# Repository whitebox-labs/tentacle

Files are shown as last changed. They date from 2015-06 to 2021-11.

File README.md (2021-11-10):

# Whitebox Labs Tentacle Shield for Arduino
`Models T1.15A, T1.16`

Tentacle Shield

## What's the Tentacle Shield?
An Arduino shield to host and individually isolate up to 4 EZO Circuits from Atlas Scientific to measure PH, Dissolved Oxygen, Electric Conductivity (E.C.), Oxidation-Reduction Potential (ORP) and RTD (Temperature).

* 4 channels
* 5V only

Individually isolated measurement circuits and communication lines prevent noise and ground loops for precise measurements even in closed-loop systems.

## Getting Started
* [Documentation Site](https://www.whiteboxes.ch/docs/tentacle/t1)
* Download the [Setup Sketch](https://raw.githubusercontent.com/whitebox-labs/tentacle-examples/master/arduino/tentacle-setup/tentacle_setup/tentacle_setup.ino)
* [Quick Start Tutorial](https://www.whiteboxes.ch/docs/tentacle/t1/#/quickstart)

## Code Examples
* [Continuous readings](https://www.whiteboxes.ch/docs/tentacle/t1/#/continuous-example)
* [Continuous, asynchronous readings](https://www.whiteboxes.ch/docs/tentacle/t1/#/asynchronous-example)
* [Interactive, bidirectional communications](https://www.whiteboxes.ch/docs/tentacle/t1/#/interactive-example)
* [Examples Git Repository](https://github.com/whitebox-labs/tentacle-examples) `git clone https://github.com/whitebox-labs/tentacle-examples.git`
* [Download all examples (zip)](https://github.com/whitebox-labs/tentacle-examples/archive/master.zip)

## Downloads
* [Tentacle Setup sketch](https://raw.githubusercontent.com/whitebox-labs/tentacle-examples/master/arduino/tentacle-setup/tentacle_setup/tentacle_setup.ino)
* [T1.16 3D-Model (STL)](https://github.com/whitebox-labs/tentacle/blob/master/hardware/mechanical/tentacle_t1.STL)
* [T1.16 3D-Model (STEP)](https://github.com/whitebox-labs/tentacle/blob/master/hardware/mechanical/tentacle_t1.STEP)
* [T1.16 Mechanical Drawing (PDF)](https://github.com/whitebox-labs/tentacle/raw/master/hardware/mechanical/tentacle_t1_mechanical.pdf)
* [BNC Connector Mechanical Drawing (PDF)](https://github.com/whitebox-labs/tentacle/raw/master/hardware/mechanical/bnc_mechanical.pdf)
* [T1.16 Schematic (PDF)](https://github.com/whitebox-labs/tentacle/raw/master/hardware/tentacle_schematic.pdf)

## Support
For customer support, please use the [contact form](https://www.whiteboxes.ch/contact/) on our website.

If you find bug in the documentation, examples or the schematic, feel free to create an issue or even a pull request here on GitHub. 

## Open Source
The Tentacle Shield is [certified](http://certificate.oshwa.org/certification-directory/) Open Source Hardware with UID CH000003. Schematics and layout are licensed under [Creative Commons BY-SA 4.0](http://creativecommons.org/licenses/by-sa/4.0/). Silkscreen graphics and the trade mark “Tentacle” are intellectual property of Whitebox Labs

* [Hardware source files on GitHub](https://github.com/whitebox-labs/tentacle) `git clone https://github.com/whitebox-labs/tentacle.git`

Made with KiCAD logo (http://kicad.org/)

## Buy
* From [our store](https://www.whiteboxes.ch/) – we ship worldwide
* or from one of our [Distributors](https://www.whiteboxes.ch/distributors)

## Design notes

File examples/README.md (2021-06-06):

examples moved here:

https://github.com/whitebox-labs/whitebox-arduino-example-code

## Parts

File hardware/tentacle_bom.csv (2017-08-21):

Id | Description | Package | Qty | Designator | Designation
1 | 1x6-pin female header .1inch | .1 inch header | 1 | SHIELD1 | ARDUINO_SHIELD
2 | 1x8-pin female header .1inch | .1 inch header | 2 | SHIELD1 | ARDUINO_SHIELD
3 | 1x10-pin female header .1inch | .1 inch header | 1 | SHIELD1 | ARDUINO_SHIELD
4 | LDO voltage regulator | SOT89 | 4 | REG1,REG2,REG3,REG4 | LD2981ABU50TR
5 | UART multiplexer | SO16N | 1 | MUX1 | 74HCT4052D122
6 | Digital signal isolator | so-8 | 4 | SIG_ISO2,SIG_ISO3,SIG_ISO4,SIG_ISO1 | SI8600
7 | SMD resistor 4.7K, 1/8W | SM0805 | 19 | R16,R14,R12,R10,R8,R6,R4,R2,R17,R3,R1,R7,R5,R9,R11,R13,R15,R18,R19 | 4.7K
8 | Multilayer Ceramic Capacitor 0.1uF | SM0805 | 8 | C4,C9,C14,C19,C10,C5,C15,C20 | 0.1 µF
9 | Multilayer Ceramic Capacitor 1uF | SM0805 | 8 | C12,C2,C7,C17,C1,C6,C11,C16 | 1µF
10 | Multilayer Ceramic Capacitor 2.2uF | SM0805 | 4 | C3,C8,C13,C18 | 2.2µF
11 | Tantalum Capacitor 470uF | c_tant_x | 1 | C21 | 470µF
12 | 1x3 male pin headers .1inch | 1x3 .1 inch spacing male pin | 1 | JP9 | JUMPER3
13 | 2x3 male pin headers .1inch | 2x3 .1 inch spacing male pin | 4 | JP1,JP3,JP5,JP7,JP2,JP4,JP6,JP8 | JUMPER3
14 | Tactile push button | B3S-1000P | 1 | SW1 | SW_PUSH
15 | Isolated DC/DC converter 5V | R1SE_0505 | 4 | DCDC1,DCDC2,DCDC3,DCDC4 | R1SE_0505
16 | BNC Connector | BNC-1337542 | 4 | P1,P2,P3,P4 | BNC
17 | 1x3-pin female header .1inch | 1x3 .1 inch spacing female pin | 8 | STP1,STP2,STP3,STP4 | ATLAS_STAMP
18 | Shorting jumper .1inch | .1 inch jumper | 9 | JP* | JUMPER, JUMPER3

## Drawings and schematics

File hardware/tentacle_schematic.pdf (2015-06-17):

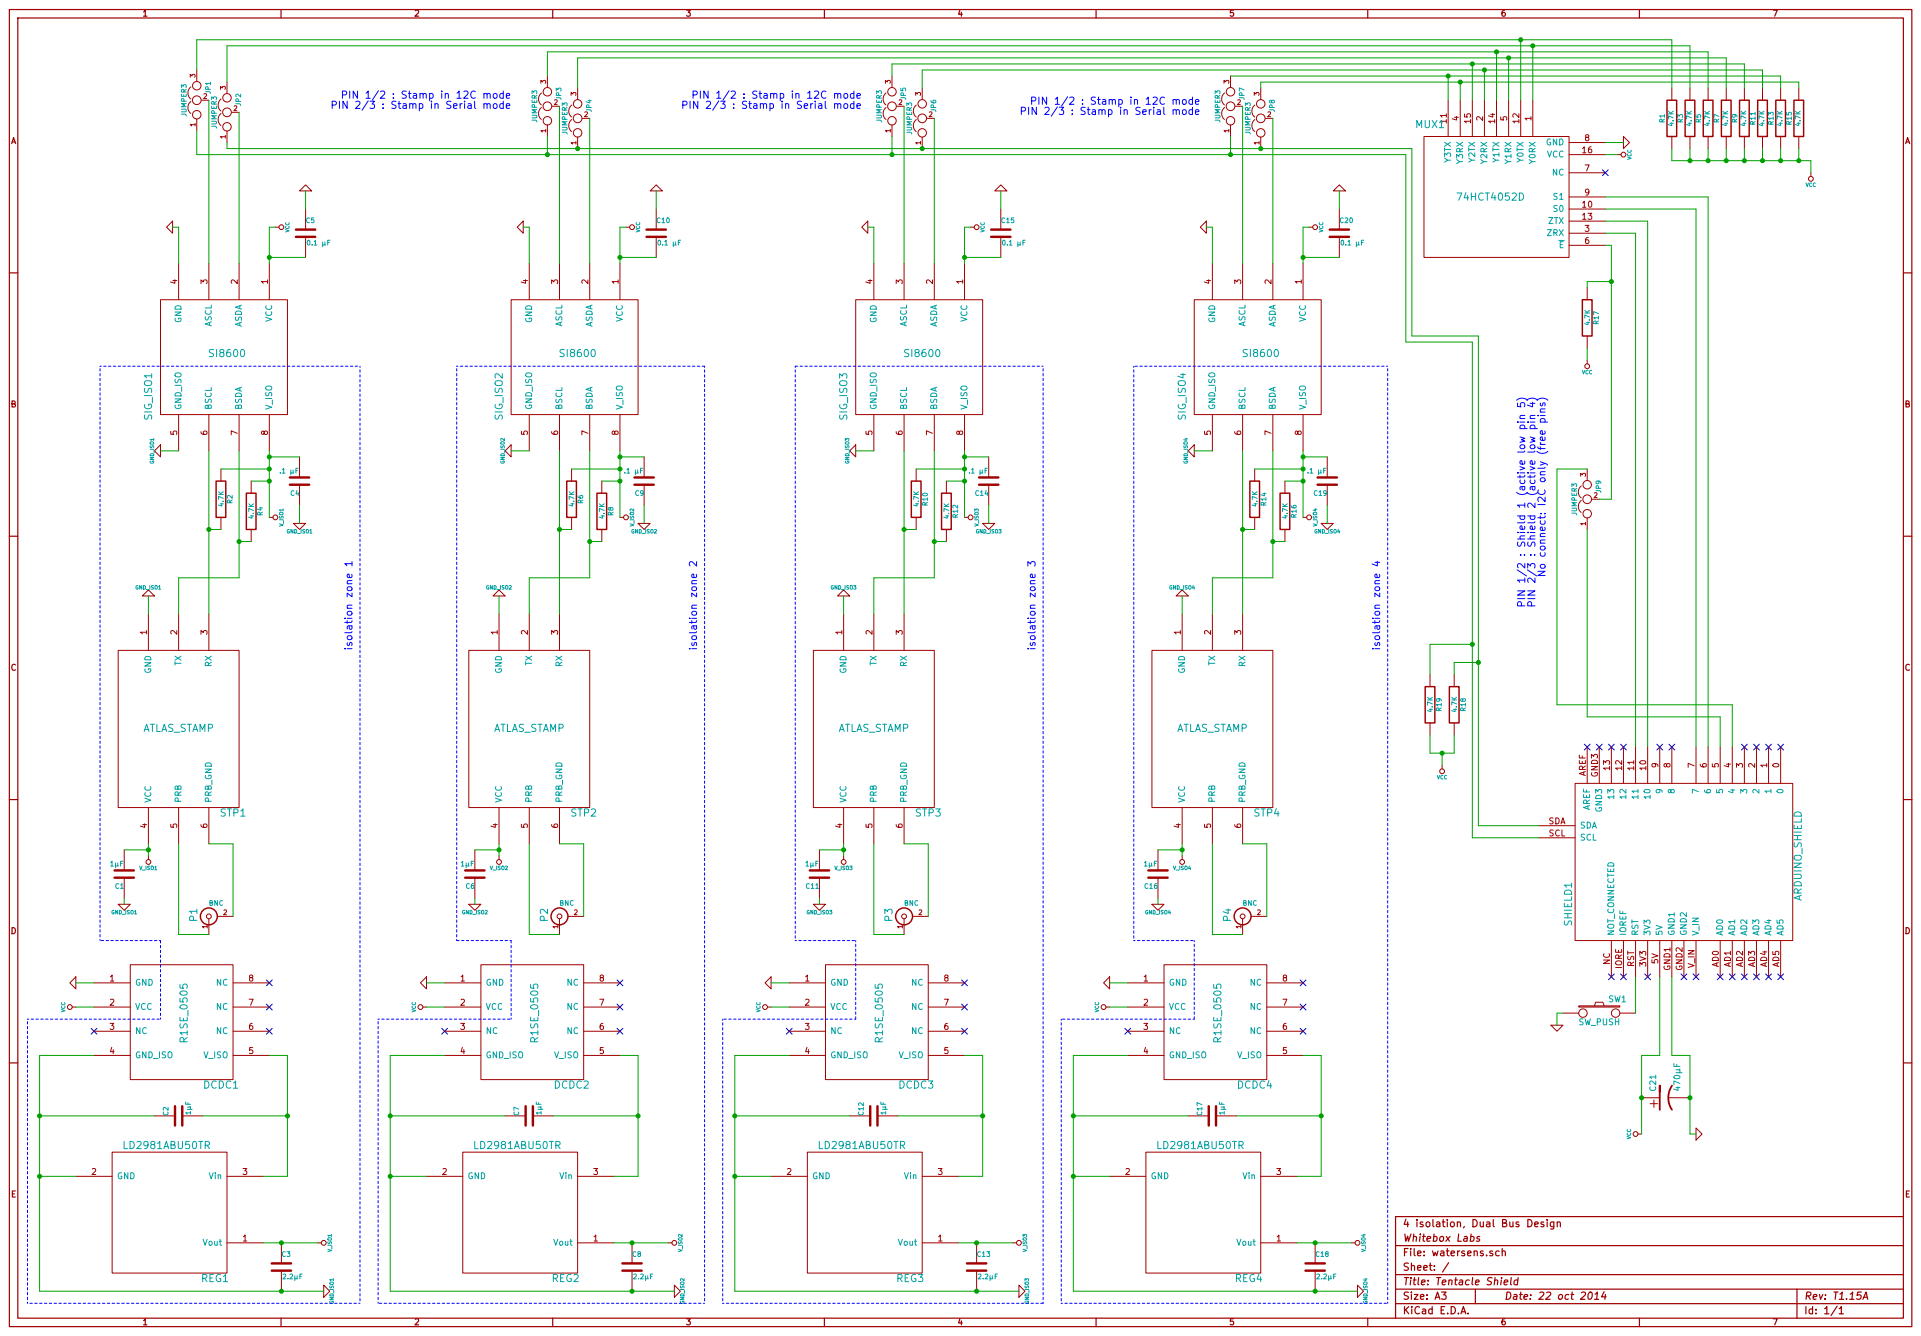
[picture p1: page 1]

3 JP7 JUMPER3
Title: Tentacle Shield File: watersens.sch Sheet: / Whitebox Labs 4 isolation, Dual Bus Design Y0RX

PIN 1/2 : Stamp in 12C mode
PIN 2/3 : Stamp in Serial mode

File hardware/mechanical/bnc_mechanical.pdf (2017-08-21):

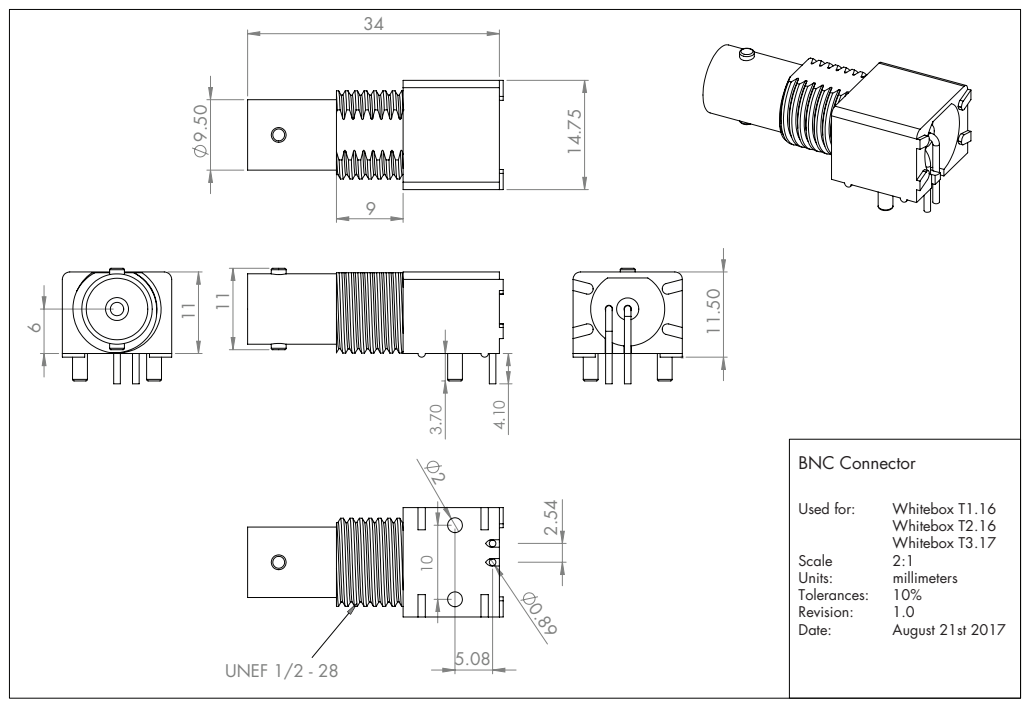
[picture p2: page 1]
UNEF 1/2 - 28; BNC Connector; Used for:; Whitebox T1.16; Whitebox T2.16 Whitebox T3.17; Scale; Units:; millimeters; Tolerances:; Revision:; Date:; August 21st 2017

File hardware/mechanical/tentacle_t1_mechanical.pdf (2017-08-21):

50.80 | 77.40

1.30

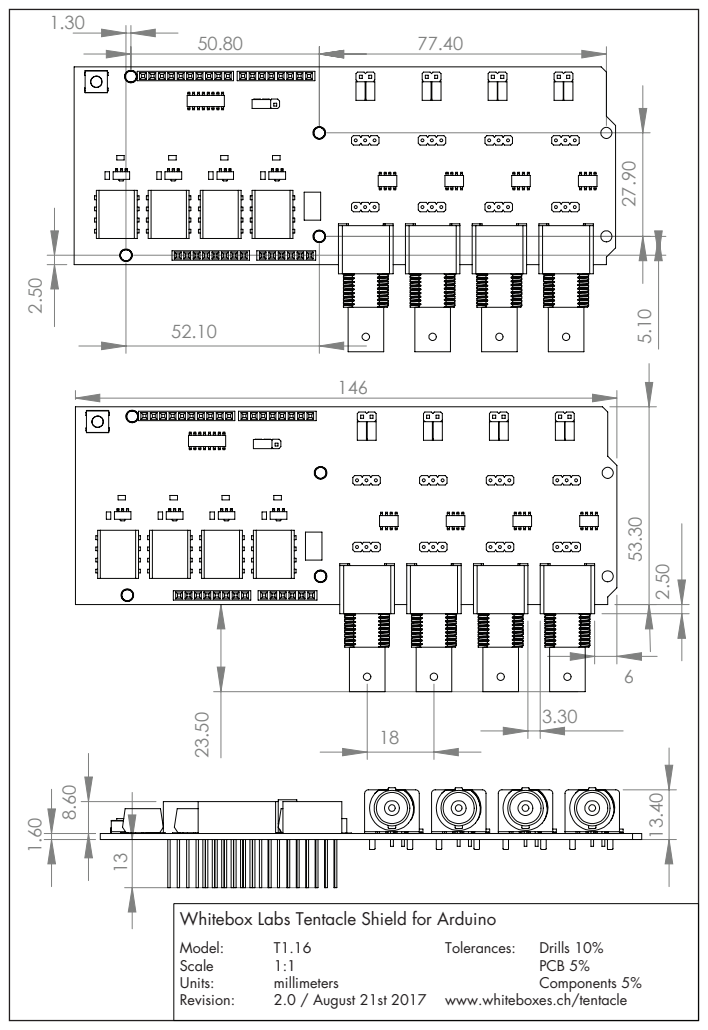
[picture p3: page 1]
Tolerances:; Drills 10%; PCB 5% Components 5%; Model:; Scale; Units:; millimeters; Revision:; 2.0 / August 21st 2017

Whitebox Labs Tentacle Shield for Arduino

www.whiteboxes.ch/tentacle

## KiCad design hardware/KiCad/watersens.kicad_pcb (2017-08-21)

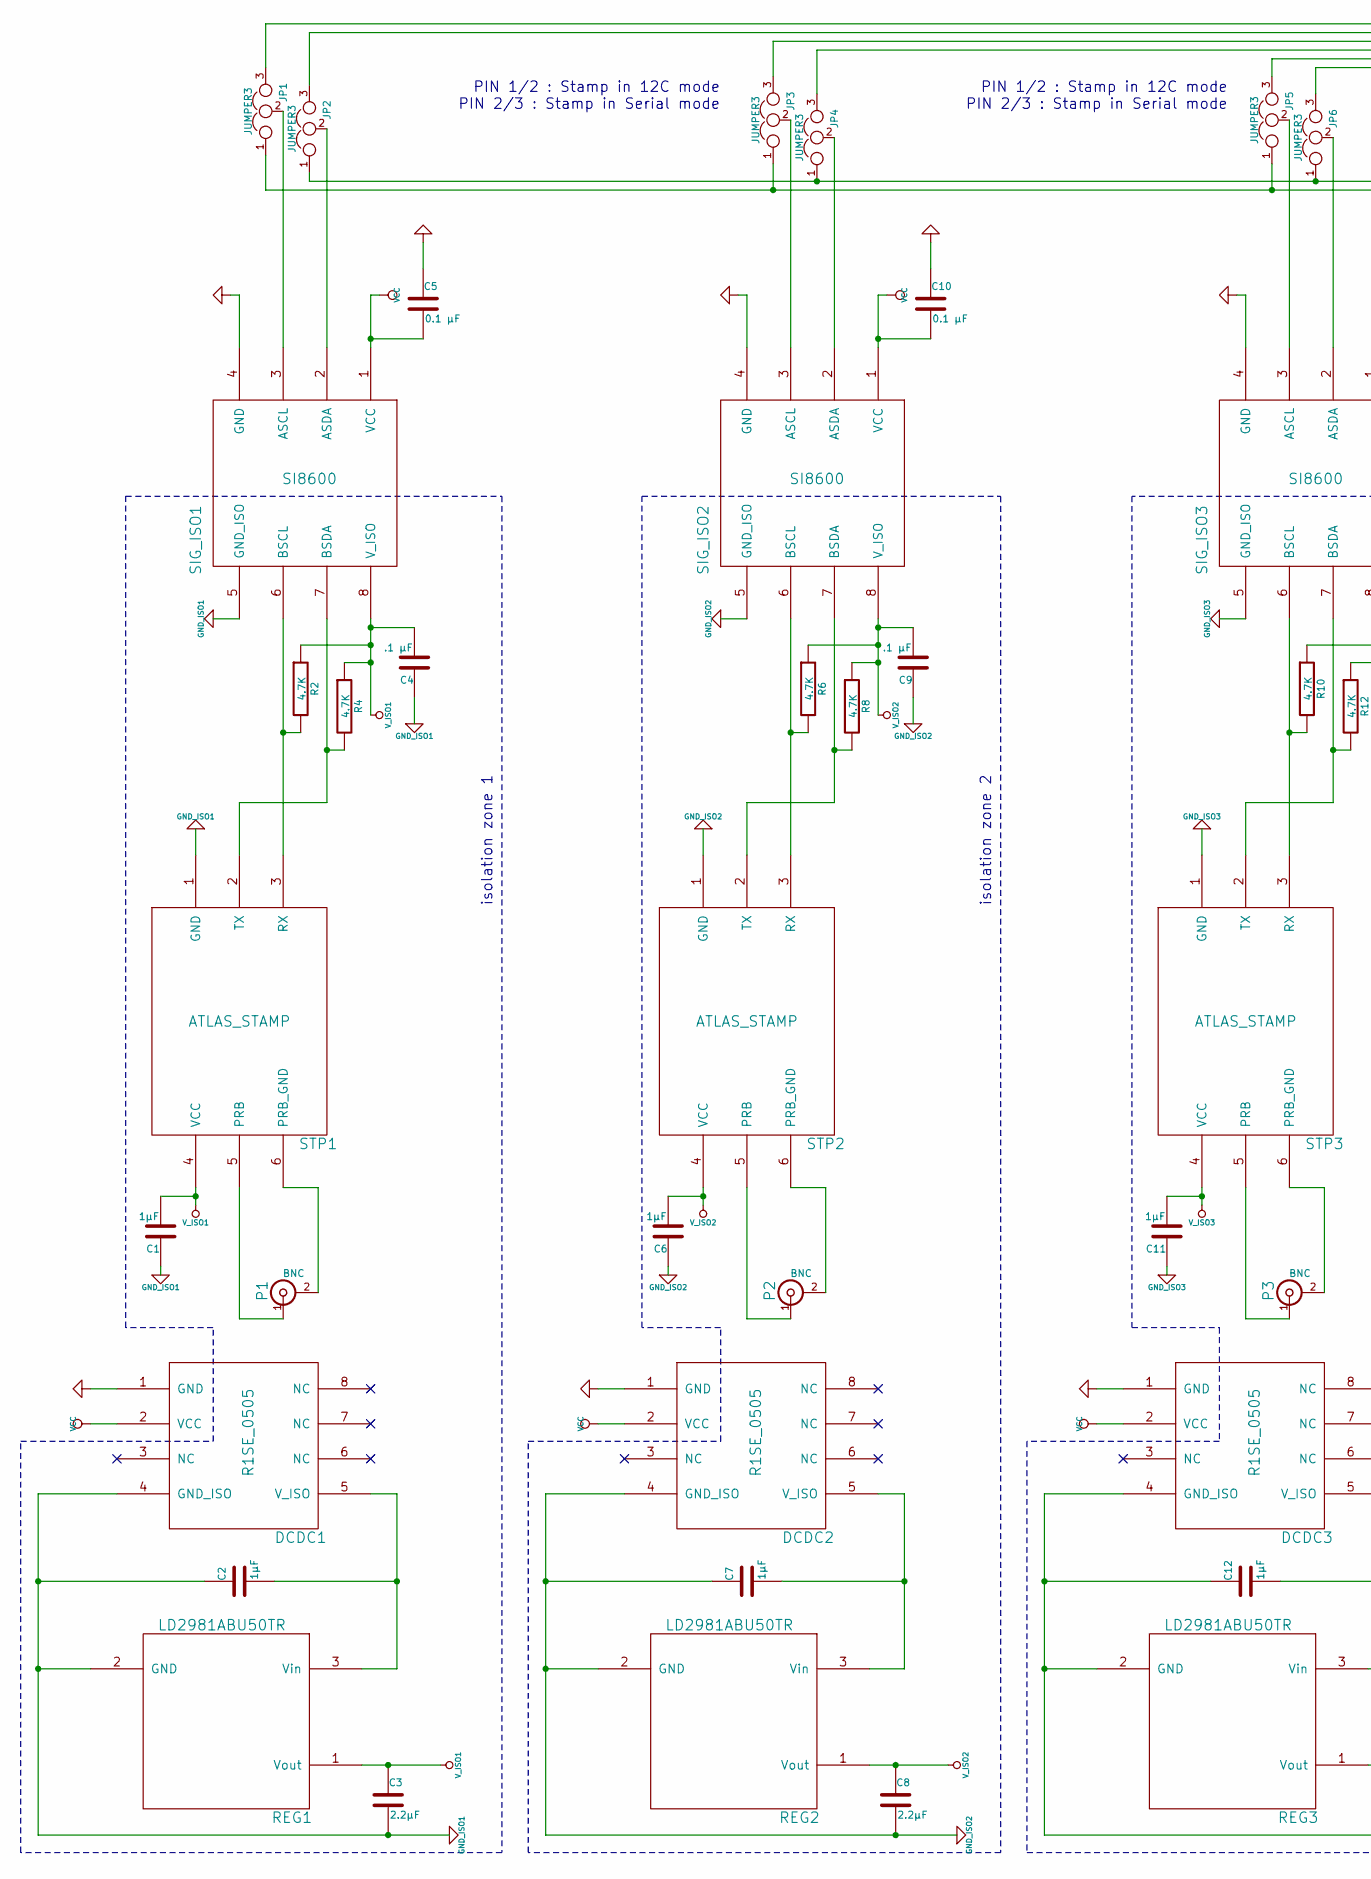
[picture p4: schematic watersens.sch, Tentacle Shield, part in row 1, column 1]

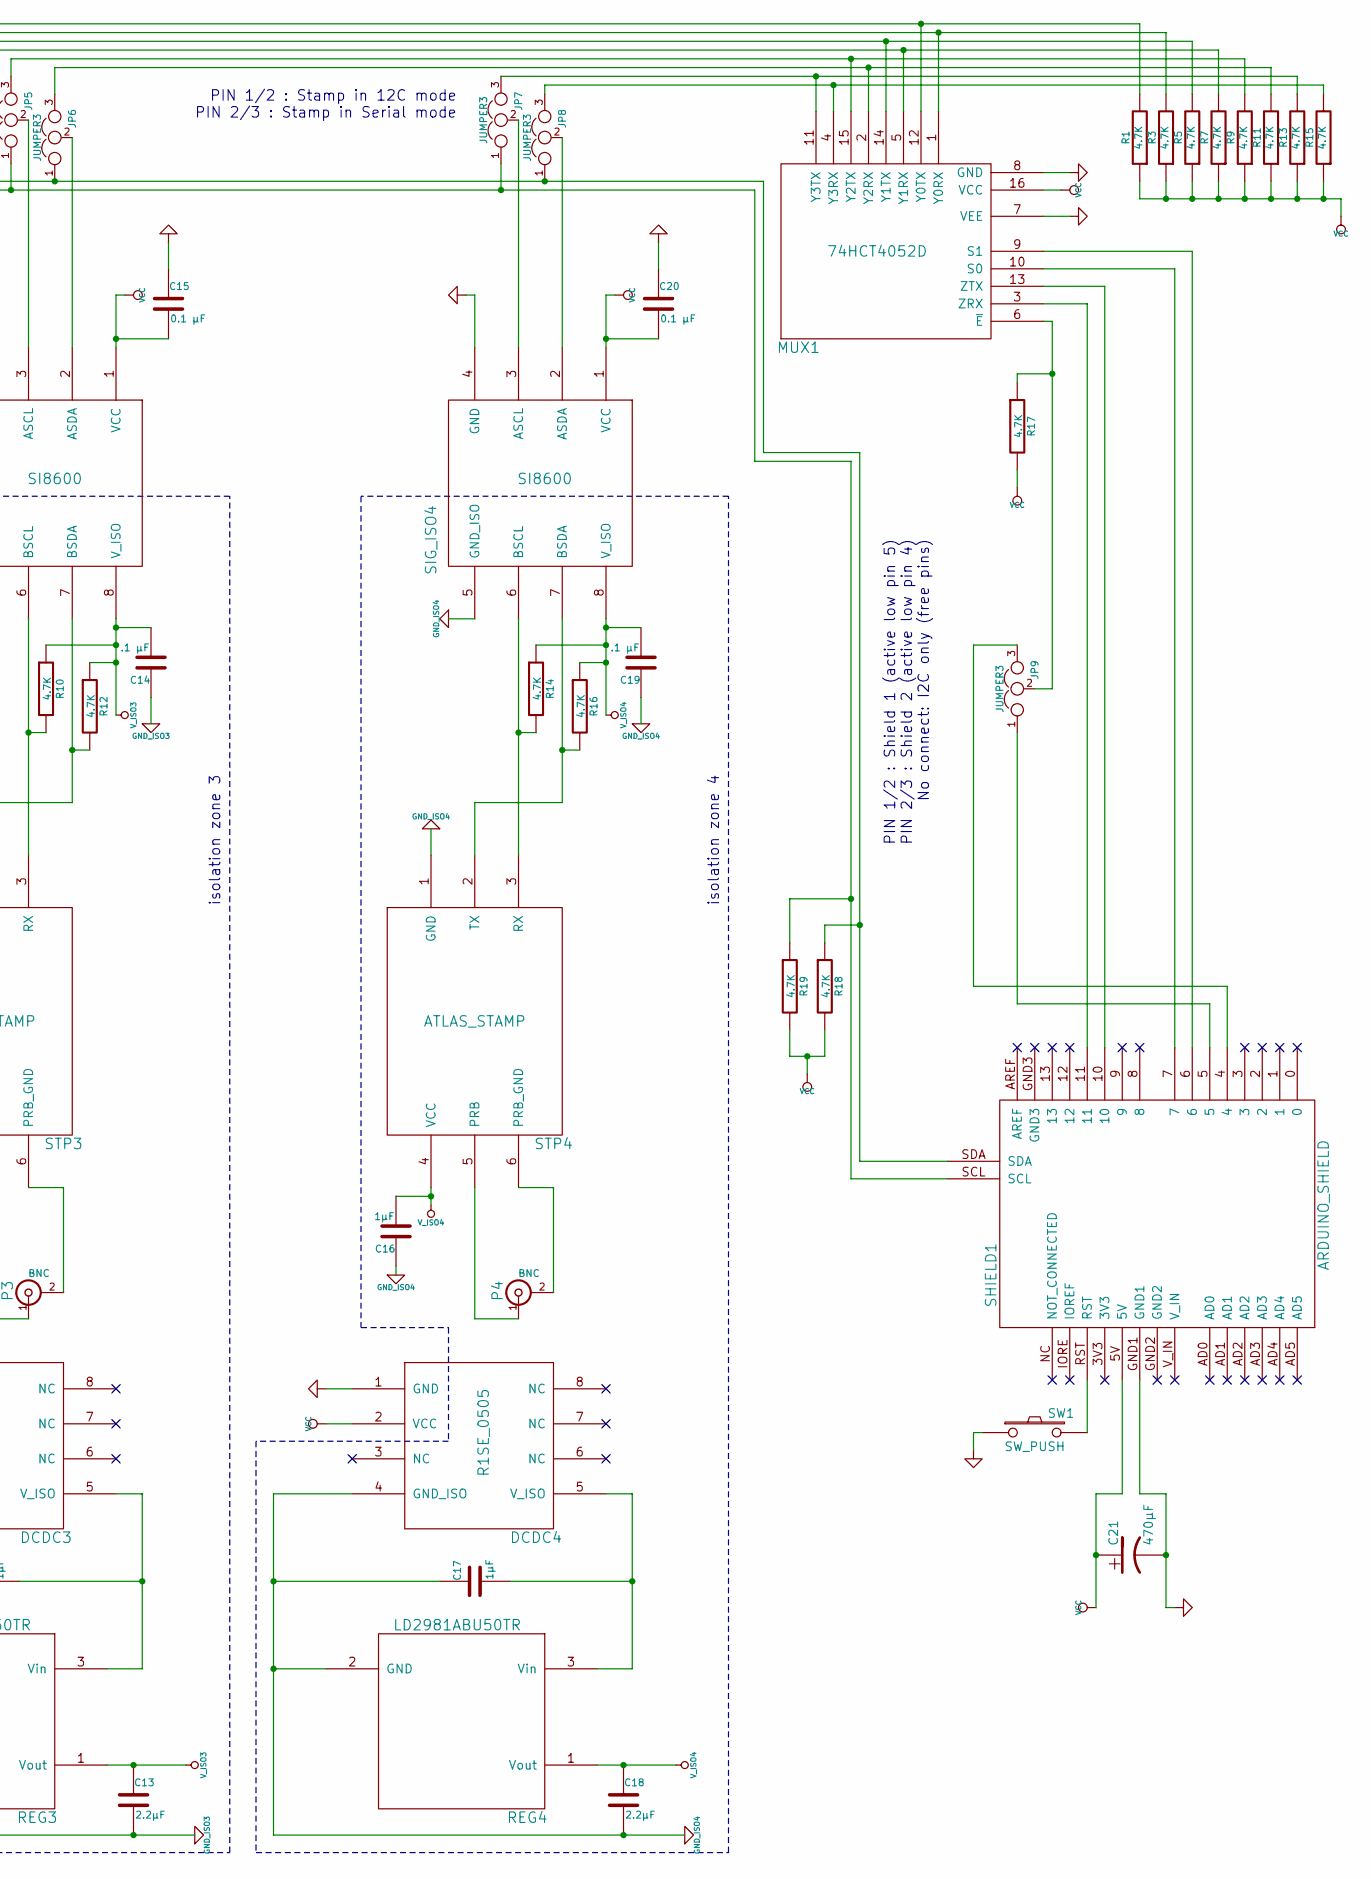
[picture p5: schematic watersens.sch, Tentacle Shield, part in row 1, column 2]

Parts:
C1, C6, C11, C16: 1µF; SM0805a
C2, C7, C12, C17: 1µF; SM0805
C3, C8, C13, C18: 2.2µF; SM0805
C4, C9, C14, C19: .1 µF; SM0805a
C5, C10, C15, C20: 0.1 µF; SM0805a
C21: 470µF; c_tant_X
DCDC1, DCDC2, DCDC3, DCDC4: R1SE_0505
JP1, JP2, JP3, JP4, JP5, JP6, JP7, JP8, JP9: JUMPER3; PINHEAD1-3a
MUX1: 74HCT4052D; SO16N
P1, P2, P3, P4: BNC; BNC-1337543a
R1, R2, R3, R4, R5, R6, R7, R8, R9, R10, R11, R12, R13, R14, R15, R16, R18, R19: 4.7K; SM0805a
R17: 4.7K; SM0805
REG1, REG2, REG3, REG4: LD2981ABU50TR; sot89
SHIELD1: ARDUINO_SHIELD; ARDUINO_SHIELD_040pinsa_no_outline
SIG_ISO1, SIG_ISO2, SIG_ISO3, SIG_ISO4: SI8600; so-8a
STP1, STP2, STP3, STP4: ATLAS_STAMP; Atlas_Stamp
SW1: SW_PUSH; B3S-1000P

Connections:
GND: C5.1, C10.1, C15.1, C20.1, C21.2, DCDC1.1 (GND), DCDC2.1 (GND), DCDC3.1 (GND), DCDC4.1 (GND), MUX1.7 (VEE), MUX1.8 (GND), SHIELD1.GND1, SIG_ISO1.4 (GND), SIG_ISO2.4 (GND), SIG_ISO3.4 (GND), SIG_ISO4.4 (GND), SW1.1
GND_ISO1: C1.1, C2.1, C3.2, C4.1, DCDC1.4 (GND_ISO), REG1.2 (GND), SIG_ISO1.5 (GND_ISO), STP1.1 (GND)
GND_ISO2: C6.1, C7.1, C8.2, C9.1, DCDC2.4 (GND_ISO), REG2.2 (GND), SIG_ISO2.5 (GND_ISO), STP2.1 (GND)
GND_ISO3: C11.1, C12.1, C13.2, C14.1, DCDC3.4 (GND_ISO), REG3.2 (GND), SIG_ISO3.5 (GND_ISO), STP3.1 (GND)
GND_ISO4: C16.1, C17.1, C18.2, C19.1, DCDC4.4 (GND_ISO), REG4.2 (GND), SIG_ISO4.5 (GND_ISO), STP4.1 (GND)
unnamed: C2.2, DCDC1.5 (V_ISO), REG1.3 (Vin)
unnamed: C7.2, DCDC2.5 (V_ISO), REG2.3 (Vin)
unnamed: C12.2, DCDC3.5 (V_ISO), REG3.3 (Vin)
unnamed: C17.2, DCDC4.5 (V_ISO), REG4.3 (Vin)
unnamed: JP1.1, JP3.1, JP5.1, JP7.1, R19.1, SHIELD1.SCL
unnamed: JP1.2, SIG_ISO1.3 (ASCL)
unnamed: JP1.3, MUX1.12 (Y0TX), R1.2
unnamed: JP2.1, JP4.1, JP6.1, JP8.1, R18.1, SHIELD1.SDA
unnamed: JP2.2, SIG_ISO1.2 (ASDA)
unnamed: JP2.3, MUX1.1 (Y0RX), R3.2
unnamed: JP3.2, SIG_ISO2.3 (ASCL)
unnamed: JP3.3, MUX1.14 (Y1TX), R5.2
unnamed: JP4.2, SIG_ISO2.2 (ASDA)
unnamed: JP4.3, MUX1.5 (Y1RX), R7.2
unnamed: JP5.2, SIG_ISO3.3 (ASCL)
unnamed: JP5.3, MUX1.15 (Y2TX), R9.2
unnamed: JP6.2, SIG_ISO3.2 (ASDA)
unnamed: JP6.3, MUX1.2 (Y2RX), R11.2
unnamed: JP7.2, SIG_ISO4.3 (ASCL)
unnamed: JP7.3, MUX1.11 (Y3TX), R13.2
unnamed: JP8.2, SIG_ISO4.2 (ASDA)
unnamed: JP8.3, MUX1.4 (Y3RX), R15.2
unnamed: JP9.1, SHIELD1.5
unnamed: JP9.2, MUX1.6 (~E), R17.1
unnamed: JP9.3, SHIELD1.4
unnamed: MUX1.3 (ZRX), SHIELD1.11
unnamed: MUX1.9 (S1), SHIELD1.6
unnamed: MUX1.10 (S0), SHIELD1.7
unnamed: MUX1.13 (ZTX), SHIELD1.10
unnamed: P1.1 (In), STP1.5 (PRB)
unnamed: P1.2 (Ext), STP1.6 (PRB_GND)
unnamed: P2.1 (In), STP2.5 (PRB)
unnamed: P2.2 (Ext), STP2.6 (PRB_GND)
unnamed: P3.1 (In), STP3.5 (PRB)
unnamed: P3.2 (Ext), STP3.6 (PRB_GND)
unnamed: P4.1 (In), STP4.5 (PRB)
unnamed: P4.2 (Ext), STP4.6 (PRB_GND)
unnamed: R2.2, SIG_ISO1.6 (BSCL), STP1.3 (RX)
unnamed: R4.2, SIG_ISO1.7 (BSDA), STP1.2 (TX)
unnamed: R6.2, SIG_ISO2.6 (BSCL), STP2.3 (RX)
unnamed: R8.2, SIG_ISO2.7 (BSDA), STP2.2 (TX)
unnamed: R10.2, SIG_ISO3.6 (BSCL), STP3.3 (RX)
unnamed: R12.2, SIG_ISO3.7 (BSDA), STP3.2 (TX)
unnamed: R14.2, SIG_ISO4.6 (BSCL), STP4.3 (RX)
unnamed: R16.2, SIG_ISO4.7 (BSDA), STP4.2 (TX)
unnamed: SHIELD1.RST, SW1.2
VCC: C5.2, C10.2, C15.2, C20.2, C21.1, DCDC1.2 (VCC), DCDC2.2 (VCC), DCDC3.2 (VCC), DCDC4.2 (VCC), MUX1.16 (VCC), R1.1, R3.1, R5.1, R7.1, R9.1, R11.1, R13.1, R15.1, R17.2, R18.2, R19.2, SHIELD1.5V, SIG_ISO1.1 (VCC), SIG_ISO2.1 (VCC), SIG_ISO3.1 (VCC), SIG_ISO4.1 (VCC)
V_ISO1: C1.2, C3.1, C4.2, R2.1, R4.1, REG1.1 (Vout), SIG_ISO1.8 (V_ISO), STP1.4 (VCC)
V_ISO2: C6.2, C8.1, C9.2, R6.1, R8.1, REG2.1 (Vout), SIG_ISO2.8 (V_ISO), STP2.4 (VCC)
V_ISO3: C11.2, C13.1, C14.2, R10.1, R12.1, REG3.1 (Vout), SIG_ISO3.8 (V_ISO), STP3.4 (VCC)
V_ISO4: C16.2, C18.1, C19.2, R14.1, R16.1, REG4.1 (Vout), SIG_ISO4.8 (V_ISO), STP4.4 (VCC)

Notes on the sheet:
PIN 1/2 : Shield 1 (active low pin 5) PIN 2/3 : Shield 2 (active low pin 4) No connect: I2C only (free pins)
PIN 1/2 : Stamp in 12C mode PIN 2/3 : Stamp in Serial mode
isolation zone 1
isolation zone 2
isolation zone 3
isolation zone 4

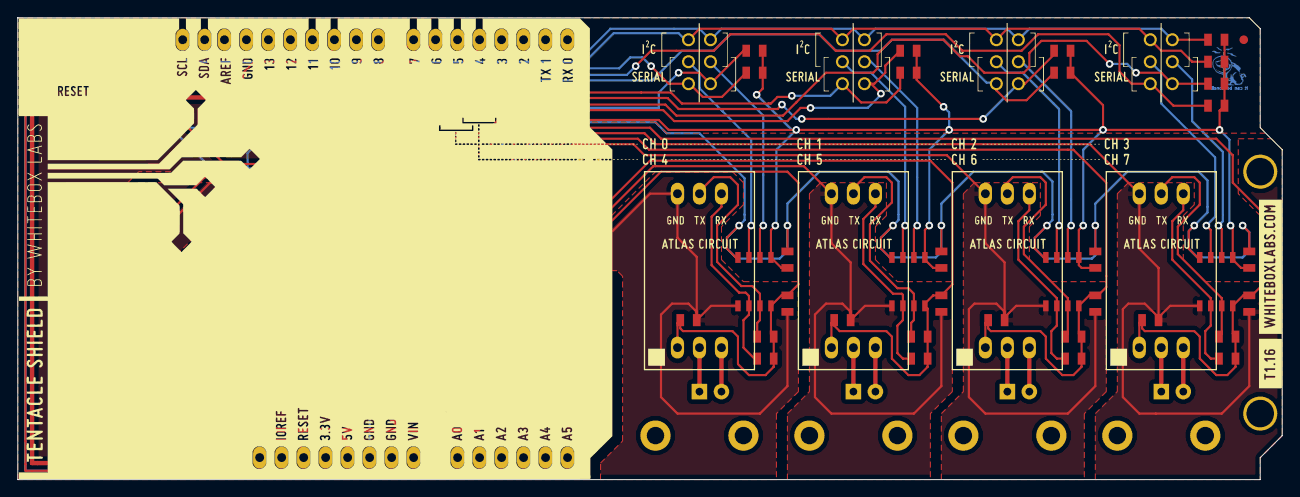
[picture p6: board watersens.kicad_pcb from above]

Board: 2 copper layers, 146.1 x 53.3 mm, 77 parts (0 on the bottom side), 56 nets.

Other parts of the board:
VAL: REF; 141029_back_V2_highres_B.SilkS_146mm_flipped
VAL#2: REF; icon
VAL#3: REF; 141029_front_V3_highres_F.SilkS_146mm
fiducial: VAL**; fiducial
fiducial#2: VAL**; fiducial

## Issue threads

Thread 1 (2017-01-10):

### ISSUE TITLE
Test RaspberryPi compatibility

### ISSUE THREAD

**Issue by extrapixel** [whitebox-labs/tentacle#1]
via connection bridge etc. If compatible, make wiring and coding examples.

**Comment by ShaneKirkbride** [comment]
I tested this configuration. It is compatible with the 2 port board at least.

**Comment by extrapixel** [comment]
Confirmed compatible with a level-shifter. However, consider using the new Tentacle T3 for Raspberry Pi for simpler connection to the Pi.

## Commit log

2015-06-17 removed old arduino module
2015-06-17 remove lib reference to arduino V3 folder
    update libs, regen net list, resync along the eeschema-netlist-PCBnew
    chain.
2015-06-17 update schema/rename bom
    [tentacle_bom.csv]
2015-07-15 short pin 7 on mux to ground.
    update schematic, netlist, PCB, fills, and plots.
    [watersens-B_Cu.gbl, watersens-B_Mask.gbs, watersens-B_SilkS.gbo, watersens-Edge_Cuts.gbr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]
2015-07-15 update component lib pin labels
    update labels, update to chain.
    [watersens-B_Cu.gbl, watersens-B_Mask.gbs, watersens-B_SilkS.gbo, watersens-Edge_Cuts.gbr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]
2015-10-12 netlist
    I re-added the netlist from backup
    removed *.net from .gitignore
    netlist needed to link schmatic to pcb design
2015-10-16 T1.16
    added art, removed edges from shield mod SilkS, added previews
    [watersens-B_Cu.gbl, watersens-B_Mask.gbs, watersens-B_SilkS.gbo, watersens-Edge_Cuts.gbr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]
2015-10-17 removed silkscreen from components
    [watersens-B_Cu.gbl, watersens-B_Mask.gbs, watersens-B_SilkS.gbo, watersens-Edge_Cuts.gbr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]
2015-10-29 cleaned up gerber files structure.
    [watersens-B_Cu.gbl, watersens-B_Mask.gbs, watersens-B_SilkS.gbo, watersens-Edge_Cuts.gbr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]
2015-11-23 added command "scani2c" to scan i2c devices only. added license. updated usage instructions.
2015-11-23 added command "scani2c" to scan for i2c devices only. added license. updated usage instructions. changed host baudrate to 9600. cleanup.
2015-11-23 added examples for Arduino Yun
2015-11-27 changed pin definitions in schematic parts
    changed pin definitions in schematic parts metadata for improved error
    checking,
    [watersens.sch]
2015-12-07 changed sketch to use 4 circuits. updated IDs to use circuit factory settings.
2015-12-08 fab file
    .pos file added to gerbs folder
    -drills/positioning origin set to lower left feducial
    -regen gerbs, drills and .pos
    -.pos settings : mm scale, 1 file per board, no force
    [watersens-B_Cu.gbl, watersens-B_Mask.gbs, watersens-B_SilkS.gbo, watersens-Edge_Cuts.gbr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]
2015-12-08 drastically simplified. continuous sensor readings.
2015-12-15 update pos file
    -update the attributes of SMD footprints to 'Normal + Insert'
    -update module lib files.
    -regen gerbs, drills and pos files
    -checked for other parts with missing attributes. C_tant_x SWx and DCDCx
    corrected.
    [watersens-B_Cu.gbl, watersens-B_Mask.gbs, watersens-B_SilkS.gbo, watersens-Edge_Cuts.gbr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]
2015-12-15 fixed UART communication to work with old or slow circuits
2016-01-08 setup tool for SAM based arduinos (Zero, Due, etc) only for Tentacle Mini
2016-05-09 added EZO RTD to the auto-detection. fixed circuit names.
2016-05-10 compatibility optimizations
    tested to work with
    T1: UNO, Mega, leonardo, yun
    T2: UNO, Mega, leonardo, yun, Zero
    Note: not compatible with Arduino 101.
2016-09-18 Update for KiCad v4
    [watersens.kicad_pcb, watersens.sch]
2016-09-18 Remove files no longer used
    [watersens-B_Cu.gbl, watersens-B_Mask.gbs, watersens-B_SilkS.gbo, watersens-Edge_Cuts.gbr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]
2016-09-18 Regenerate gerber files
    [watersens-B.Cu.gbl, watersens-B.Mask.gbs, watersens-B.SilkS.gbo, watersens-Edge.Cuts.gm1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]
2017-08-21 added detail drawing for BNC connectors
2017-08-21 updated BOM
    [tentacle_bom.csv]
2021-11-09 Update README.md
    https://forum.kicad.info/t/warning-avoid-all-links-to-kicad-pcb-org-use-kicad-org/31521
